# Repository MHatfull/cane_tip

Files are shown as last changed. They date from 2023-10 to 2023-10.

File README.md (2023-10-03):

# 3D printable white cane tip

This project is to make it more cost effective to replace the tip of a white cane when it wears out.

## The problem
When using a cane tip, they wear out in weeks with heavy use. The constant contact with the ground wears them down into a point and then they start to snag on every imperfection in the pavement.

To replace the tip, you would normally end up replacing both the roller ball, bearing and hook mechanism which poses several problems.
* If you accidentally let go of the elastic that runs through the cane whilst changing the tip, this can be very fiddly to retrieve.
* It is wasteful to throw away the parts that are still in good working order.

## This solution
This project aims to address these issues by making it easy to produce the cane tip yourself. If you, or someone you know, has a 3D printer then you should be able to replace the worn out tip without buying a new one. The cost of 3D filament is about 1/10th that of the price of the official tips. A small benefit is that you may prefer to choose your own colour or material, as you'll be making the tip then you have total control.

# Instructions
## What you'll need
* A standard rollerblade bearing (22mm x 7mm)
* A 3D printer
* The toughest filament you can find
* A piece of string

## How to make it
This comes in 3 parts. The insert, a washer and the tip. Fitting the insert initially can be a bit fiddly but should only need to be done once. The tip can then be reprinted over and over and fitted onto the bearing whenever it needs replacing.

1. Print 2 copies of the insert. You'll want to slice this lying on the long flat face so the layer lines aren't going to shear with the force on the tip.
1. Print the washer. This is so the cane doesn't press directly onto the bearing and stop it from rotating freely.
1. Print the tip. You can do this with the large flat surface face down. Use as many perimeters as you can, I use 12. The more the better as these are what will wear away as the cane is in use.
1. Insert the bearing into the large hole in the tip. It will be tight, this is on purpose so it doesn't come off in use. You may have to use a vice or similar tool to push it hard enough, you may be able to do it by pressing hard against a hard surface.
1. Push the 2 pieces of insert, back-to-back, through the bearing.
1. Push the washer over the insert with the thicker side facing the bearing.
1. Pull on the old cane tip until you see a white piece of plastic pop out the end of the cane. This is to hold the elastic in place while you change the tip and goes back into the cane later.
1. Remove the old tip.
1. Pass the string through the elastic in the cane, and then through the holes in the insert. Tie a knot so it forms a loop connecting the insert to the elastic. This will secure the bearing to the cane.
1. Lower the new tip into the cane.

When you need to replace the tip, you can press a metal tool through the hole in the bottom of the tip in order to remove it from the bearing and press a new tip onto the bearing.

# Disclaimer

Anyone using the information or files supplied here does so at their own risk. I take no responsibility for any harm or injury caused by the use of the supplied data. Users of the data should do so only when they are confident that it is safe to do so. There are risks involved in using the cane tip such as (but not limited to) breakage of the cane tip leaving the user stranded or the cane tip not reacting in the way the user expects. I recommend practicing with the cane tip inside in a safe, well known environment before using it elsewhere. The cane tip should only be used by sufficiently trained or competent individuals. The cane tip has been designed to work with Ambutech hook stlye canes but is not affiliated with Ambutech in any way.

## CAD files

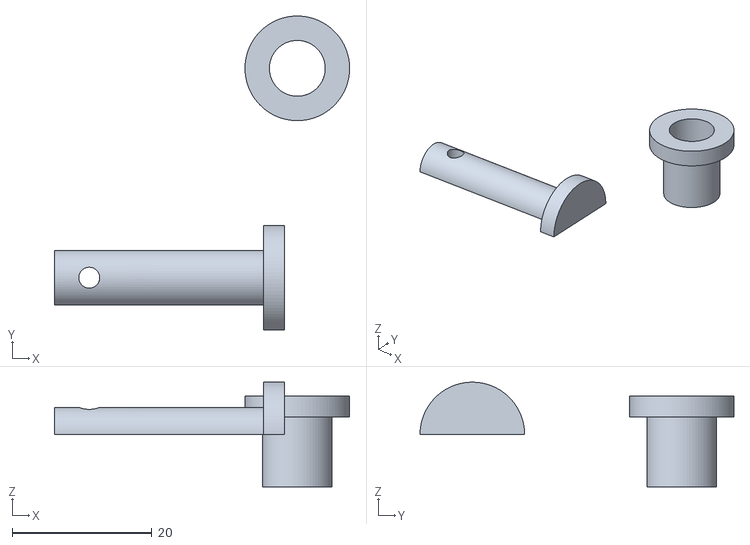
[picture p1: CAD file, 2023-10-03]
files/insert.stl
42.3 x 45.0 x 15.0

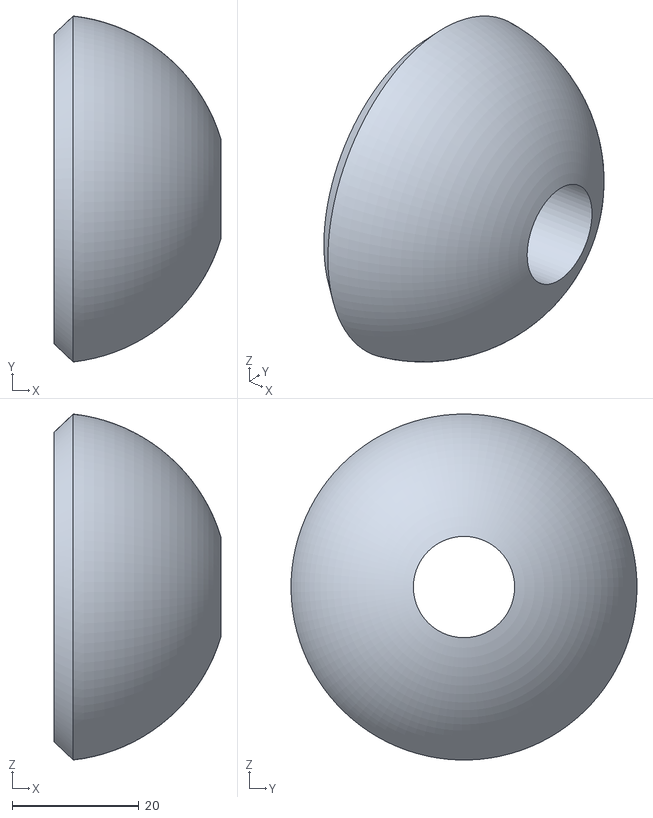
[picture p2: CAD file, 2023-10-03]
files/tip.stl
26.3 x 54.7 x 54.7

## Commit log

2023-06-27 Add 3D models to files directory
    [insert.stl, tip.stl]
2023-10-03 New version that holds the bearing and is more effient with material
    [insert.stl, tip.stl]
